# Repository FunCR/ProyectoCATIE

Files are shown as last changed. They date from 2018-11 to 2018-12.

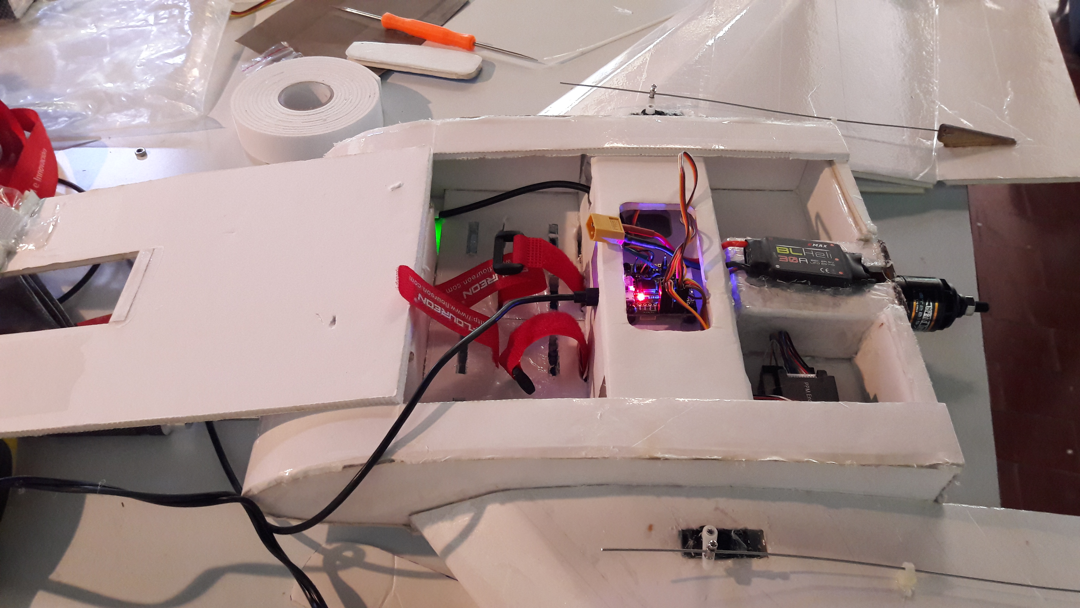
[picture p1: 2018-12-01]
FotosCatie/Montajes del controlador y administrador de energia/Montaje sin Administrador de energia.jpg

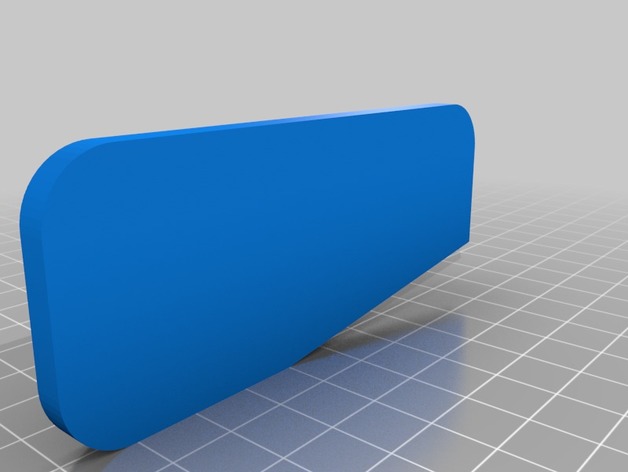
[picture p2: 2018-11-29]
DronAlaFIja/FT_spear_wing_angle_tools/images/22f3830a188973f9ce258d5c663154c2_preview_featured.jpg

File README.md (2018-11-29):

# ProyectoCATIE
Repositorio de documentos, reportes, códigos y archivos digitales de fabricación para el Proyecto FunCR-CATIE

## Directorios

Los directorios en este repositorio contienen todos los archivos del proyecto, desde infromes hasta códigos y diseños para fabricación.

* TreeScan: Archivos del prototipo de escaner de rodales. Incluye diseños fotos y codigos
* QuadLidar: Archivos para el chasis y el dispositivo LIDAR para adaptar al Quad
* DronAlaFija: Archivos de fabricación e instrucciones para la construcción del dron de ala fija
* FotosCATIE: repositorio de fotos del proyecto
* Informes: Informes y documentos generados para el proyecto

Creado por Fundación Costa Rica para la Innovación

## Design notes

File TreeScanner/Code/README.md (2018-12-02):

# Código

* LIDAR_Scanner2: contiene los archivos de programación del microcontrolador en C/C++. Para cargarlo en microcontrolador usar Arduino IDE

* LIDAR_Viewer: Contiene l código en Processing (JAVA), para visualización de datos provenientes del escáner.  El algoritmo comienza a detectar las estructuras grandes, a partir de la cual se pueden determinar árboles.

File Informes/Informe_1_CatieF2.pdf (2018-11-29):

### Informe de acciones basado en la

### Propuesta Conceptual del desarrollo de tecnologías para la

fabricación de instrumentos para la medición de áreas basales, diámetros y altura total, distribución y dispersión de árboles.

Informe elaborado por Tomás de Camino Beck Agosto, 2018

## Índice

Antecedentes | 2
Proceso de Ideación | 3
Validación de Datos con Experto | 3
Revisión de Tecnologías Disponibles | 5
Cuadro Generador de Ideas | 8
Propuesta de Instrumentos | 10
Cronograma | 15
Recomendaciones | 16
Referencias | 16

## Antecedentes

Uno de los retos principales en mensura forestal con el advenimiento de nuevas tecnologías de menor costo y mucho más accesibles, es la de hacer mediciones cada vez rápidas y confiables en campo, y establecer relaciones con variables a nivel de paisaje, que asistan en la toma de decisiones y proyecciones de manejo de bosques.

La tecnología de microcontroladores ha mostrado que se pueden construir instrumentos confiables a gran escala , la discusión ya no está en el “si se pueden

1234
construir”, sino más bien “qué debemos construir”. Inicialmente es más sencillo pensar en tecnologías que reemplazan prácticas de mensura forestal, sin embargo el uso de estas tecnologías probablemente sugerirá nuevas formas de medir variables en bosques, y establecer relación entre variables a escala de rodal y variables a escala de paisaje.

La tecnología LIDAR permite medir distancias mediante un láser que genera pulsos de luz. Esta tecnología que hace algunos años era inaccesible, hoy en día se puede adquiere a costos menores a los $150 y puede ser utilizado para diferentes tipos de medición como altura de árboles . En esta fase nos concentramos principalmente en la

56
exploración de LIDAR y su uso en diferentes contextos

1
""Evaluating the Effects of Projected Climate Change on Forest Fuel ...." http://repository.uwyo.edu/uwnpsrc_reports/vol37/iss1/10/. Se consultó el 31 jul.. 2018.
2
"Digital stereovision system for dendrometry, georeferencing and data ...." https://www.sciencedirect.com/science/article/pii/S1537511018303180. Se consultó el 31 jul.. 2018.

3
"Edge-to-Stem Variability in Wet-Canopy Evaporation From an Urban ...." https://link.springer.com/article/10.1007/s10546-017-0277-7. Se consultó el 31 jul.. 2018.

4
"Observed compression of in situ tree stems during freezing ...." 15 sept.. 2017, https://www.sciencedirect.com/science/article/pii/S0168192317301570. Se consultó el 31 jul.. 2018.

5
"Dense Canopy Height Model from a low-cost photogrammetric ...." 15 feb.. 2016, https://link.springer.com/article/10.1007/s00468-016-1366-9. Se consultó el 31 jul.. 2018.

6
"Comparing Terrestrial Laser Scanning (TLS) and Wearable ... - MDPI." 1 abr.. 2018, http://www.mdpi.com/2072-4292/10/4/540. Se consultó el 31 jul.. 2018.

Este informe no es un tratado científico, sino más bien un reporte de la exploración de posibilidades de uso de tecnologías para generar instrumentos de medición, en particular la medición de diámetros, áreas basales y altura de árboles en un rodal. El objetivo de este proyecto fue Ideación de instrumentos de mensura forestal, específicamente para la medición de diámetros, áreas basales y alturas, a nivel de rodal.

## Proceso de ideación

La ideación consiste en la generación de posibilidades. En este proceso importa la cantidad más que la calidad. Se trabajó revisando la colección de sensores disponibles para poder determinar su posible uso. La exploración de ideas no implica el detalle técnico pues estos se resuelven en el momento de construcción y prototipado de los instrumentos.
Del mismo modo no se detallan aspectos metodológicos para el uso de los instrumento s propuestos, pues las metodologías se establecerán en el momento de prueba de cada uno de los instrumentos.
Las propuestas de instrumentos pueden variar en el proceso de construcción y validación del mismo como parte del proyecto.

Dada la utilizad de tecnologías LIDAR, se exploraron los posibles usos de esta tecnología y la posibilidad de estimar diámetros a través del movimiento del sensor para detectar los bordes de un árbol, incluyéndose alguna forma de posicionamiento relativo con un dispositivo IMU. Por esto en esta fase se explora el potencial de este dispositivo, lo que no descarta usar otras alternativas.

## Validación de Datos con experto

Se realizó una reunión con el Máster Lenin Corrales, investigador del programa de bosques de CATIE Se describieron algunas de las líneas de investigación que el programa quiere desarrollar, para explorar posibilidades de que los resultados puedan ser utilizados para el programa.

La líneas de investigación sugeridas y las posibilidades de usar tecnologías, se resúmen en el siguiente cuadro,

Línea | Tecnología Compatible
Heterogeneidad | Medición de heterogeneidad espacial con Drones
Demografía | Estructura de edades mediante lecturas de clases diamétricas con LIDAR. Crecimiento contínuo con sensores de piezoeléctricos
Fenología (Efecto de cambio climático) | Aunque está fuera de los alcances del proyecto, se podrían construir sistemas de clasificación de especies con inteligencia artificial
Fragmentación y Diversidad | Uso de LIDAR para medir la estructura y distribución espacial de los rodales
Calidad de Cobertura (Sanidad) | Posible aplicación de la fotografía en tiempo real para determinar cambios visibles en superficie de hoja. Explorar la construcción de algunos otros sensores que midan en tiempo real y alta resolución en determinados individuos dentro de un rodal.
NDVI, biodiversidad y conteo de árboles | Tecnología de LIDAR combinada con Drones para medir espectralmente y estructuralmente la composición de especies

## Revisión de Tecnologías disponibles

Tomando en cuenta las tecnologías disponibles para inicio del proyecto, se discutió con el Dr. Ronnie de Camino, especialista en manejo de bosques, los posibles usos en mensura forestal. Estos usos se detallan en el siguiente cuadro.

Equipo | Descripción | Posible uso
Raspberry Pi High-Precision 24bit AD/DA Expansion Board | Extensión para RPi, para poder hacer lecturas de hasta 24bit de resolución | Lector de sensores analógicos y conversión AD de alta precisión
Raspberry Pi | Computadora con sistema operativo Linux | ● Data Logger ● Trap Camera ● Lectura de sensores de alta precisión
Feather M0 Datalogger | Micro-controlador con procesador M0 | ● Data logger ● Lectura de multiples sensores
FeatherWing OLED | Pantalla para microcontrolador | ● Lectura en tiempo real ● Interfaz para usuario de campo
Lithium Ion Polymer Battery -3.7v 1200mAh | Baterías para microcontroladores | ● Sistemas de almacenamiento de datos en campo
SONOFF TH Sensor -DS18B20 | Swith de control remoto | ● Sistemas remotos de encendido y apagado
Adafruit TSL2591 High Dynamic Range Digital Light Sensor | Sensor de Luz | ● Sistemas de medición de luz dentro y fuera del bosque

| | ● Medición de luz visible, ultravioleta e infrarrojo desde el suelo
Adafruit Ultimate GPS Breakout - 66 channel w/10 Hz updates | Sistema de GPS de 10 lecturas por segundo | ● Construcción de GPS portátiles para colocar en dispositivos de campo
ADS1115 16-Bit ADC | Convertidor análogo digital de alta resolución | ● Lectura de instrumentos de medición analógicos de alta presición
Atmospheric Sensor Breakout - BME280 | Sensor de presión, temperatura y altitud | ● Medición de altura sobre el nive del mar, altura de árboles ● Para complementar uso de Drones
Conductive Rubber Cord Stretch Sensor + extras! | Goma que cambia resistencia con estiramiento | ● Medición en timepo real de diámetro
Flame Sensor Module | Sensor de flamas | ● Este sensor mide la radiación infraroja de llamas ● Puede ser utilizadoo para detección temprana de incendios ● detección de zonas calientes
Human Body Touch Sensor | Sensor capacitivo | ● Para construcción de instrumentos de medición
Infrared Thermometer -MLX90614 | Sensor que mide temperatura superficial mediante sensor de luz infrarroja. | ● Temperatura de superficie de suelo bajo diferentes condiciones dentro y fuera del bosque. ● Uso para clasificación de

| | uso de suelo y cobertura con Drone
Liquid Flow Meter 3/4 inch -BRASS | Medido de flujo de líquidos | ● Medición de escorrentía superficial ● Escorrentía en árboles ● Medición de flujo de corrientes de agua
Load Cell - 10kg, Straight Bar (TAL220) | Sensor de peso | ● Medición de Peso de ramás y troncos en sitio
Optical Dust Sensor -GP2Y1010AU0F | Medición de polvo y partículas suspendidas | ● Detector de humo de incendios ● Detector de polvo en campo ● Calidad de aire
Pressure-Sensitive Conductive Sheet (Velostat/Linqstat) | Material conductivo que cambia resistencia con presión | ● Medición de crecimiento en diámetro en tiempo real ● Medición de perturbaciones
Soil Humidity Sensor (Hygrometer) | Sensor de humedad de suelo | ● Medición de humedad de suelo en sitio ● Medición de micro variaciones de suelo ● Medición de evaporación de suelo
Temperature Sensor with Steel Head | Sensor de temperatura | ● Medir temperatura de suelo en tiempo real
Raindrop and Dew Sensor | Sensor de gotas y rocio | ● Medición de evapotranspiración ● Medición de humedad de superficie ● Medición de

| | condensación
Weather Meters | Estación meteorológica de bajo costo. | ● Velocidad de viento ● precipitación, ● temperatura ● presión ● Establecer red de estaciones meteorológicas de bajo costo ● Medición de micro-climas
Adafruit 9-DOF IMU Breakout - L3GD20H + LSM303 | Sistema de navegación | ● Medición de movimiento para Drones ● Determinar posición relativa para medición con LIDAR
Original PRUSA i3 MK2S 3D Printer (Assembled) | Impresora 3D | ● Construcción de estructuras para adaptar sensores ● Construcción de cajas ● Piezas para adaptar sensores a drones

En el proceso de desarrollo como parte de los informes de rendición de cuentas, se analizará algunos ejemplos del mercado para llevar a cabo comparaciones de interés.

## Cuadro Generador de Ideas

Con esta metodología se intenta pensar “fuera de la caja” y forzar el pensamiento lateral para la construcción de ideas. Las ideas generadas acá se dejan planteadas y se pueden desarrollar durante el transcurso del proyecto.

Técnica Ideación | Forma Normal | IDEA

Inversión | Técnico toma datos en campo con cinta diamétrica, clinómetro, etc | Que las mediciones ocurran en tiempo real en el árbol, es decir instrumentos insertado en árboles.
Integración | ärboles tiene placas y son medidos repetidamente, | Árboles base conectados en tiempor real y mandando datos a servidor (SigFox, LoRa) INtegrar en tiempo real con medidas de drones de altura
Extensión | Medir diámetros, áreas basales y alturas | Recoger datos microclimáticos, de terreno. Relacionar directo con dron en aire en tiempo real
Diferenciación | Se usa solamente una metodología de campo | Se miden más variables y por tanto se pueden adaptar medidiones a condiciones especiales
Agregar | MIde AB, diámetro y altura | Medición de diámetro a varias alturas para factor forma. Areas basales a varias alturas.
Restar | MIde AB, diámetro y altura | Con una medida lidar (scan) se derivan las medidas a partir de la imágen generada. Esto hace que el proceso sea de una medición

## Propuestas de Instrumentos

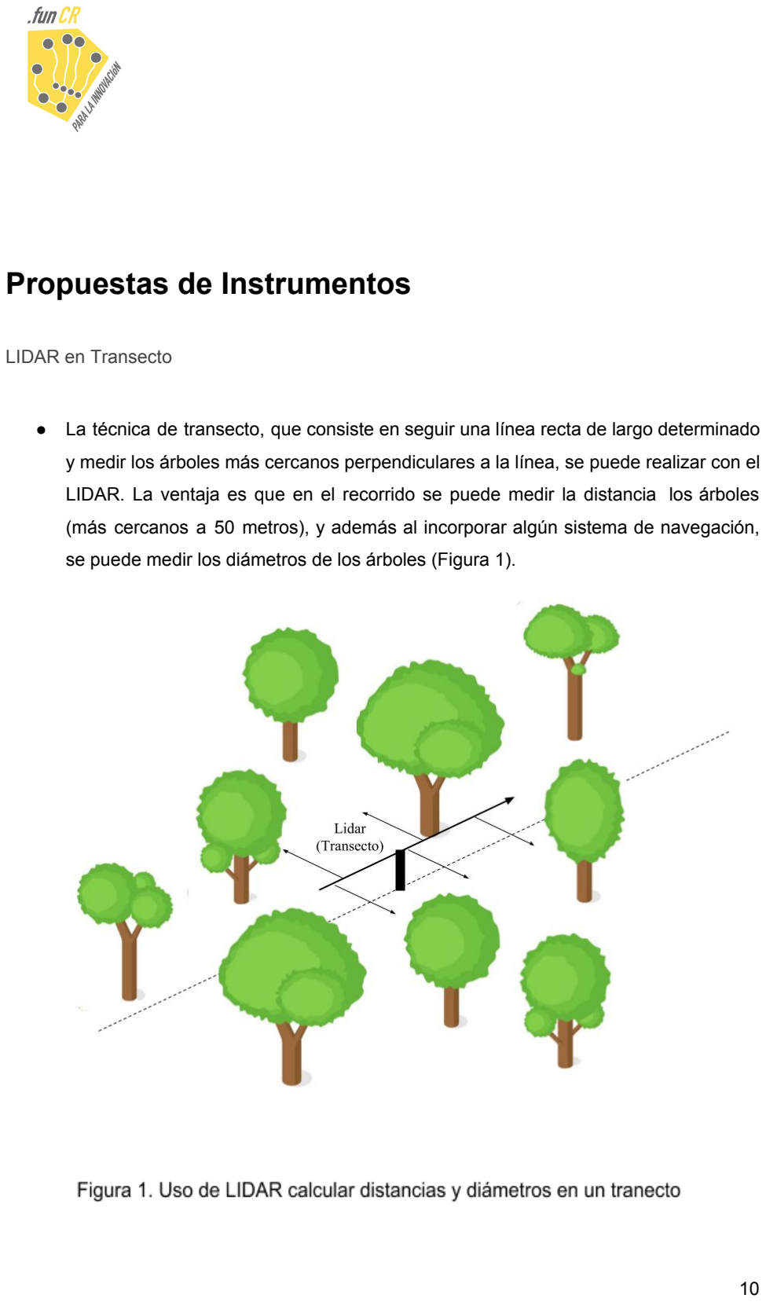
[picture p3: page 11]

LIDAR en Transecto

- La técnica de transecto, que consiste en seguir una línea recta de largo determinado y medir los árboles más cercanos perpendiculares a la línea, se puede realizar con el LIDAR. La ventaja es que en el recorrido se puede medir la distancia los árboles (más cercanos a 50 metros), y además al incorporar algún sistema de navegación, se puede medir los diámetros de los árboles (Figura 1).

- Para construir el dispositivo se debe considerar el uso de 2 LIDAR, y un acelerómetro, giroscopio y compás, para medir el movimiento, la resolución se fija en la frecuencia de lecturas del LIDAR.
- El método de muestreo consistiría en una persona caminando por el transecto demarcado, por la distancia determinada (basada en experiencia de muestreo anteriores (Figura 2).
- El método permitirá medir diámetros rápidamente, y areas basales además de la distribución espacial de los árboles.

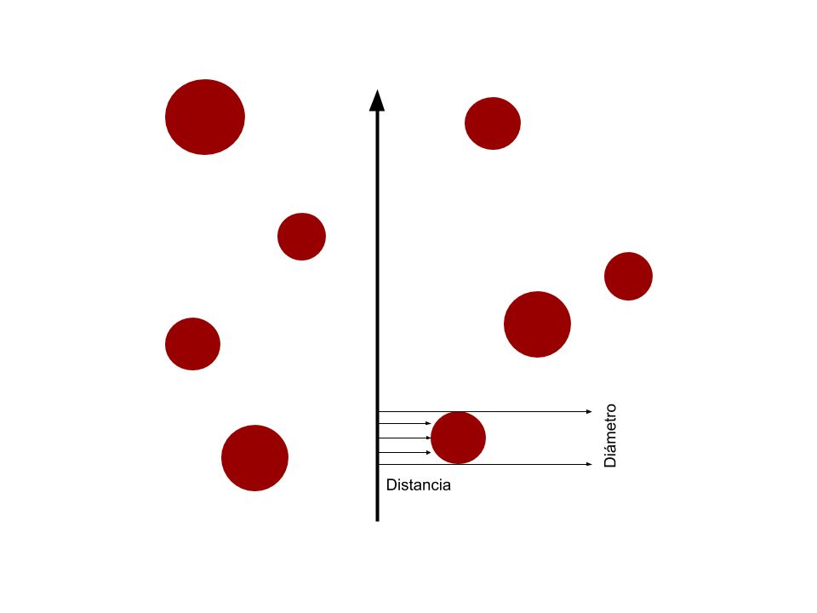
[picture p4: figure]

LIDAR Scan 360

- El lidar montado sobre un motor de paso, que permite rotación de 360 grados, permitiría escanear una nube de puntos en un plano, con la intención de obtener

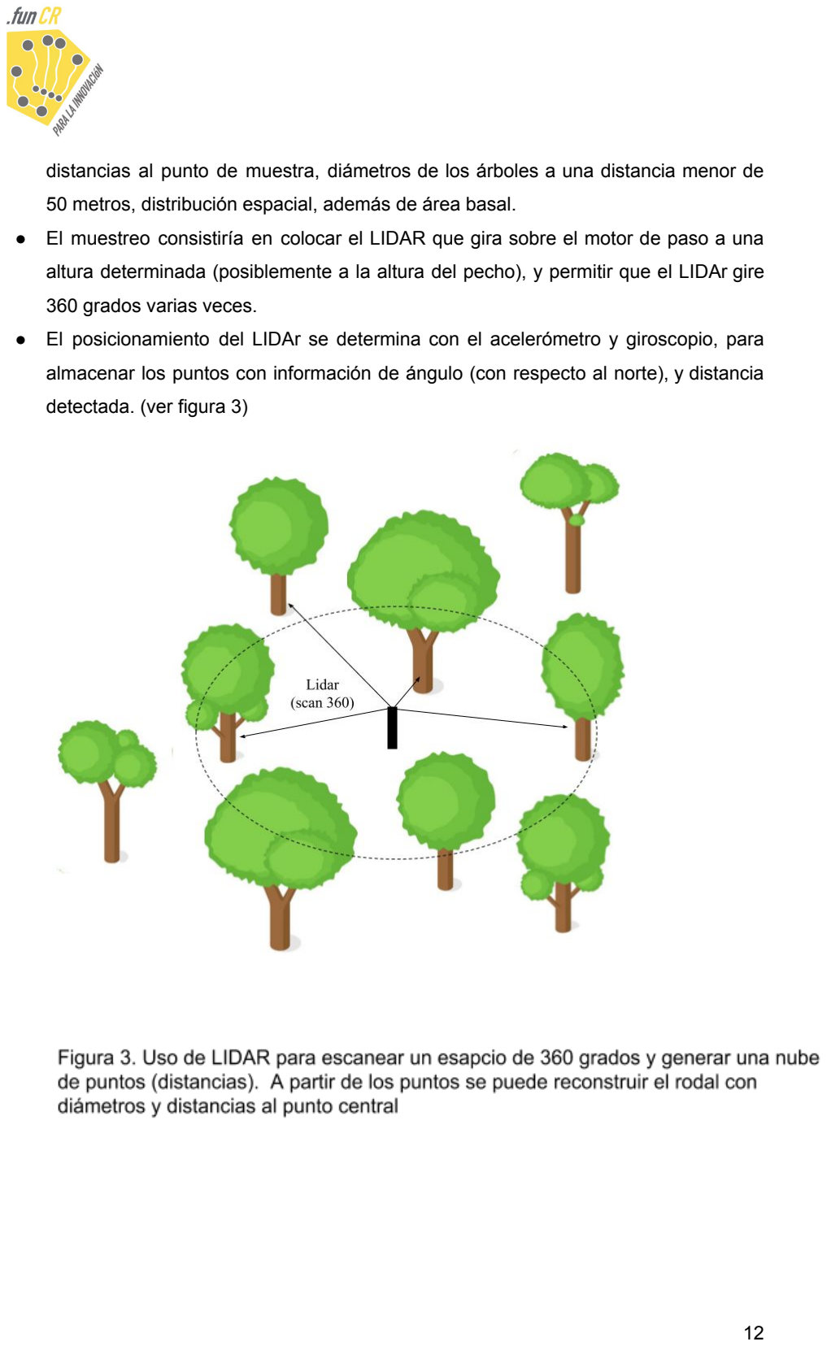
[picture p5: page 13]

distancias al punto de muestra, diámetros de los árboles a una distancia menor de 50 metros, distribución espacial, además de área basal.
- El muestreo consistiría en colocar el LIDAR que gira sobre el motor de paso a una altura determinada (posiblemente a la altura del pecho), y permitir que el LIDAr gire 360 grados varias veces.
- El posicionamiento del LIDAr se determina con el acelerómetro y giroscopio, para almacenar los puntos con información de ángulo (con respecto al norte), y distancia detectada. (ver figura 3)

- Se puede construir un sensor similar al GeoSLAM ZEB-REVO o más sofisticado

7
como el SICK LMS511 que permite escanear una nube de puntos para luego

8
reconstruir una estructura, y algunos ya se han usado para estructura vertical de bosques . La propuesta es construir un sistema, primero en 2 dimensiones, y luego

9
explorar 3D.
- Se prototipará software en porcessing.org para poder reconstruir el rodal en 2D a través de la nube de puntos

LIDAR + Drones para Altura de árboles

Como se muestra en la figura 5, ya se había explorado el uso de un LIDAR adaptado en un drone, con resultados muy preliminares indicando que si era posible medir la diferencia entre copa de árboles y el suelo.

Con el LIDAR y Drone se intentara lo siguiente:
- En vuelo controlado en un recorrido predefinido, se hará un muestreo de la información de lidar para determinar altura de árboles.
- Las alturas se calcularán por línea de vuelo
- Intento de medir un árbol con LIDAR+ drone con verificación desde el suelo
- Medición de alturas conocidas de postes para deterinar presición de medición
- Comparación con medidas de altura de Drone, GPS, y sensores de medición de altura

7
"GeoSLAM Technology - ZEB-REVO - GeoSLAM Desktop V3." https://geoslam.com/technology/. Se consultó el 31 jul.. 2018.

8
"LMS511-10100 PRO | Detection and ranging solutions SICK."
https://www.sick.com/ag/en/detection-and-ranging-solutions/2d-lidar-sensors/lms5xx/lms511-10100-pro/p/p215941. (https://www.sick.com/ag/en/detection-and-ranging-solutions/2d-lidar-sensors/lms5xx/lms511-10100-pro/p/p215941) Se consultó el 31 jul.. 2018.

9
"Efficient field data collection of tropical forest using terrestrial laser ...." https://ieeexplore.ieee.org/document/6946549/. Se consultó el 31 jul.. 2018.

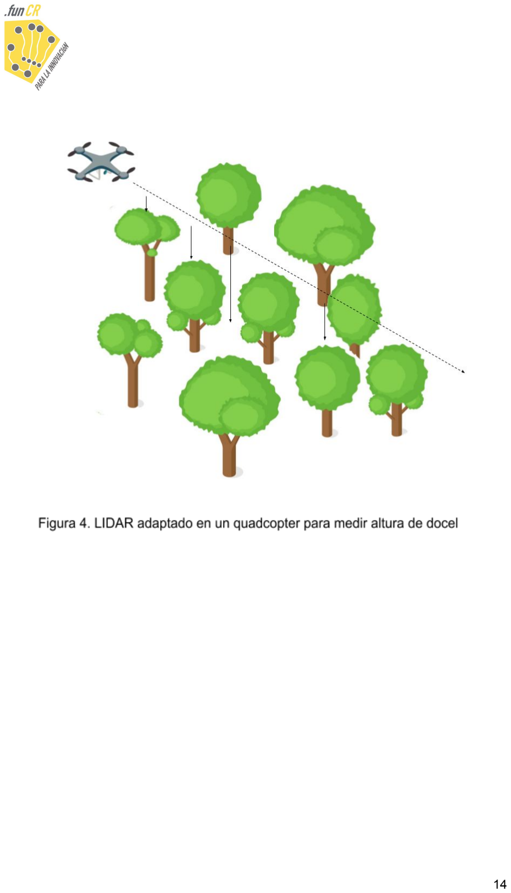
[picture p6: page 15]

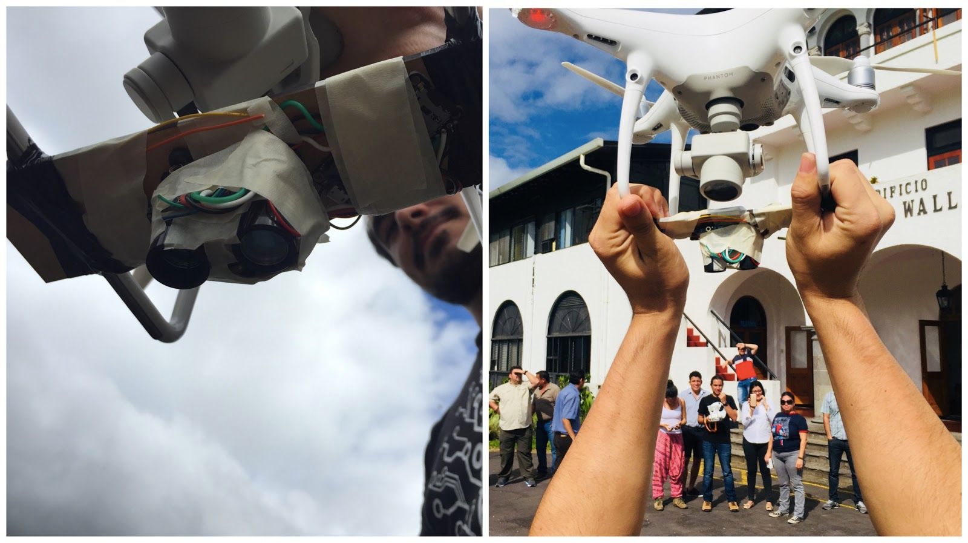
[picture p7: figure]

## Cronograma

Acción | FECHA | LOCACIÓN | ASISTENTES
Prueba de pretotipo en campo, recorrido en el bosque para evaluar características y validar funciones de la tecnología | 3 de setiembre | Turrialba, CATIE | Tomás de Camino Abraham Pineda
Prueba de prototipo de las tecnologías en campo, en dos contextos de bosque definidos por el CATIE. | 20 y 21 de setiembre | Turrialba , CATIE | Tomás de Camino Abraham Pineda
Entrega de prototipo con prueba de campo al equipo de | 8 octubre | Turrialba, CATIE | Tomas de Camino Abraham Pineda

técnico del CATIE

## Recomendaciones

- La construcción de instrumentos de medición se hará con prototipado rápido, es decir se construirá de forma progresiva.
- Se recomienda medir parcelas permanentes de medición, donde los datos sean conocidos y que se hayan hecho mediciones recientemente.
- Utilizar PPM tanto de bosques secundarios como primarios y con algún tipo de aprovechamiento forestal.
- Se debe tener claro que el uso de Drone en bosques puede presentar riesgos de accidente.
- Aunque se proponen estas técnicas, en el proceso puede surgir nuevas ideas que serán exploradas, es decir el resultado de los instrumentos para la siguiente fase puede diferir de lo planteado en este informe.
- Se debe tener claro que este es un proceso de exploración de tecnologías, como tal, las mediciones que se realicen pretenden demostrar las posibilidades tecnológicas, no la construcción de un tratado científico.
- Se debe crear un repositorio de códigos diseños e instrucciones de construcción para poder promover el uso de tecnologías abiertas en la construcción de instrumentos de mensura forestal.

## Referencias

""Evaluating the Effects of Projected Climate Change on Forest Fuel ...." http://repository.uwyo.edu/uwnpsrc_reports/vol37/iss1/10/. Se consultó el 31 jul.. 2018.
"Digital stereovision system for dendrometry, georeferencing and data ...." https://www.sciencedirect.com/science/article/pii/S1537511018303180. Se consultó el 31 jul.. 2018 "Edge-to-Stem Variability in Wet-Canopy Evaporation From an Urban ...." https://link.springer.com/article/10.1007/s10546-017-0277-7. Se consultó el 31 jul.. 2018.
"Dense Canopy Height Model from a low-cost photogrammetric ...." 15 feb.. 2016, https://link.springer.com/article/10.1007/s00468-016-1366-9. Se consultó el 31 jul.. 2018. "Observed compression of in situ tree stems during freezing ...." 15 sept.. 2017, https://www.sciencedirect.com/science/article/pii/S0168192317301570. Se consultó el 31 jul.. 2018. "Comparing Terrestrial Laser Scanning (TLS) and Wearable ... - MDPI." 1 abr.. 2018, http://www.mdpi.com/2072-4292/10/4/540. Se consultó el 31 jul.. 2018.
"GeoSLAM Technology - ZEB-REVO - GeoSLAM Desktop V3." https://geoslam.com/technology/. Se consultó el 31 jul.. 2018.

"LMS511-10100 PRO | Detection and ranging solutions SICK."
https://www.sick.com/ag/en/detection-and-ranging-solutions/2d-lidar-sensors/lms5xx/lms511-10100-pro/p/p215941. (https://www.sick.com/ag/en/detection-and-ranging-solutions/2d-lidar-sensors/lms5xx/lms511-10100-pro/p/p215941) Se consultó el 31 jul.. 2018.
"Efficient field data collection of tropical forest using terrestrial laser ...." https://ieeexplore.ieee.org/document/6946549/. Se consultó el 31 jul.. 2018.

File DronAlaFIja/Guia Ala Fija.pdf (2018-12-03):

### Guia Drones Ala Fija

# Materiales:

- 1 Kit completo cortado en carto-foam, 22 piezas en total.
- 1 Controlador de vuelo, F3 o superior.
- 1 GPS para el controlador de vuelo F3
- 1 Receptor de control remoto de 2.4 Ghz o similar.
- 1 Control remoto de 2.4Ghz o similar
- 1 Administrador de voltaje
- 1 Motor Brushless 2215 de 1050KV o superior
- 1 Controlador de velocidad de 30 amperios o superior para materias de hasta 6 celdas
- 2 Micro servos de 9.5g preferiblemente de engranaje metálico
- 4 Extensiones para servos
- Camara FPV de 600TVL o superior
- Transmisor de video de 5.8ghz de 200 miliwatts a 600 miliwatts
- Module de reception de video en 5.8 Ghz
- Monitor de video para modulo: Pueden ser los lentes Fatshark o los monitores integrados grandes
- Batería de 4 celdas de amenos 2000mah
- Placa para baterias
- Velcro
- Cinta de empaque
- Silicon
- Pistola de silicon caliente
- Cutter
- 2 Alambres de acero inoxidable calibre 20 de 30 cm de largo

# Proceso de ensamble

## Fuselaje

Una vez se cuente con el kit completo del fuselaje en cartón foam, ya sea fabricado a mano o en cortadora Láser, debe seguir el siguiente video instructivo para armar el fuselaje:

https://youtu.be/B5dqMtpdbcU

Existen dos modos de ensamble definidos por si tiene o no administración de energía.

Es necesario poner atención a los diferentes tipos de dobleces en las partes del fuselaje, en el dobles “A” las paredes caen encima de la placa central, en el dobles “B” las paredes quedan al lado de la placa central y el dobles “C” las paredes se doblan una encima de la otra.

## Controlador de Vuelo y Administrador de Energia

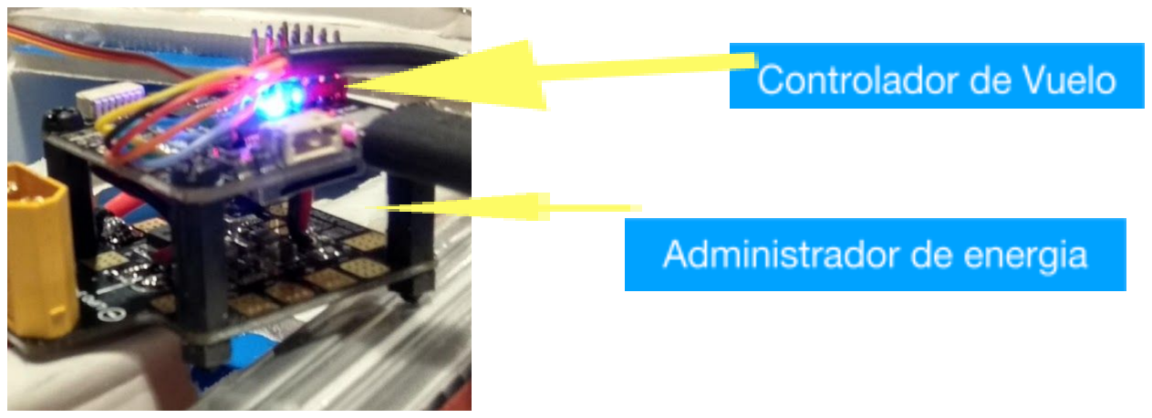
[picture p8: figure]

El video completa la versión del fuselaje preparada para la versión sin el administrador de energía. El administrador de energía y el controlador de vuelo se ensamblan en torre.

## Administrador de energia

El administrador de energía proporciona diferentes voltajes:

- Voltaje directo de la batería para los motores.
- 12 voltios para transmisor de video y tracker GPS.

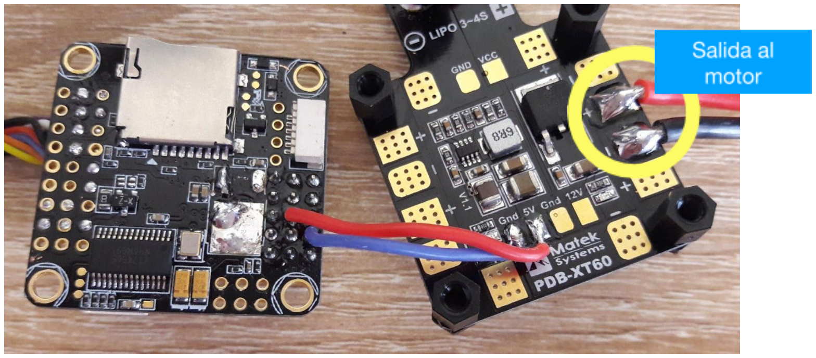
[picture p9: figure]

- 5 voltios para el controlador de vuelo, servos y otros sensores.
*Ensamble del administrador de vuelo con administrador de energía. Conexión de 5v (5 voltios) para controlador de vuelo, sensores y servos y puerto de energía al motor.

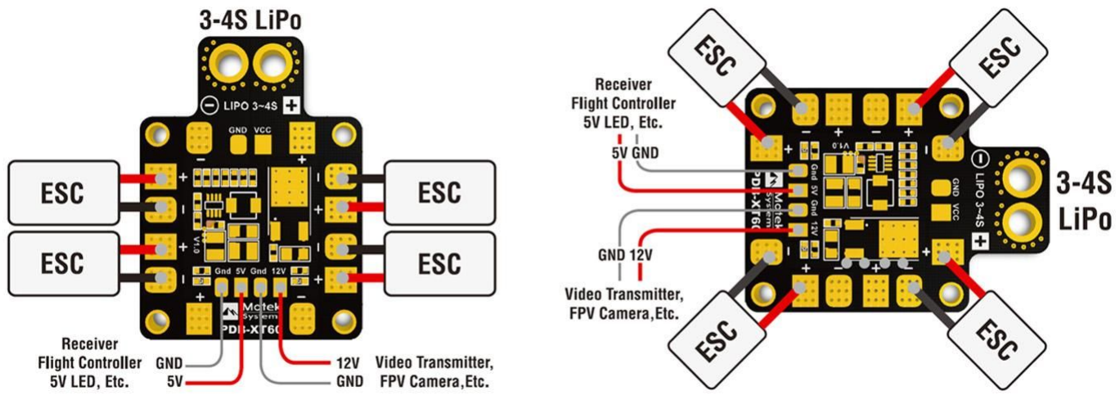
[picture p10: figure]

El administrador cuenta con puertos de energía para los ESC (controladores de velocidad del motor), transmisor de video, controlador de vuelo y otros.
*Ensamble del administrador de vuelo con administrador de energía. Conexión de 5v (5 voltios) para controlador de vuelo, sensores y servos y puerto de energía al motor.
El diagrama muestra todas las posibles conexiiones del administrador, importante tomar en cuenta que todas la conexiones son soldadas. Conectar a todas las cosas según su disposición de vuelo.

El modelo que no contiene administración de energía está dispuesto a ser una fabricación más rápida y un modelo que se puede usar para el entrenamiento de nuevos pilotos o vuelos que no requieren sensores o dispositivos que demanden mucha energía.

El administrador de energía incluye un circuito que filtra la energía para que no existe interferencia entre los diferentes sistemas presentes en el aeronave.

## Controlador de vuelo

El controlador de vuelo que estamos utilizando es de aplicación en carreras de drones, estos drones alcanzan velocidades de hasta 150 Km/h. El diseño de alta precisión y gran velocidad de procesamiento nos permite utilizar este estándar en aplicaciones que explota al máximo las posibilidades de la plataforma mientras entrega un excelente desempeño.

El controlador de vuelo es un Omnibus F3, empaquetado en una versión especial llamada Inav F3. Este controlador está dispuesto para este tipo de aplicaciones autónomas.

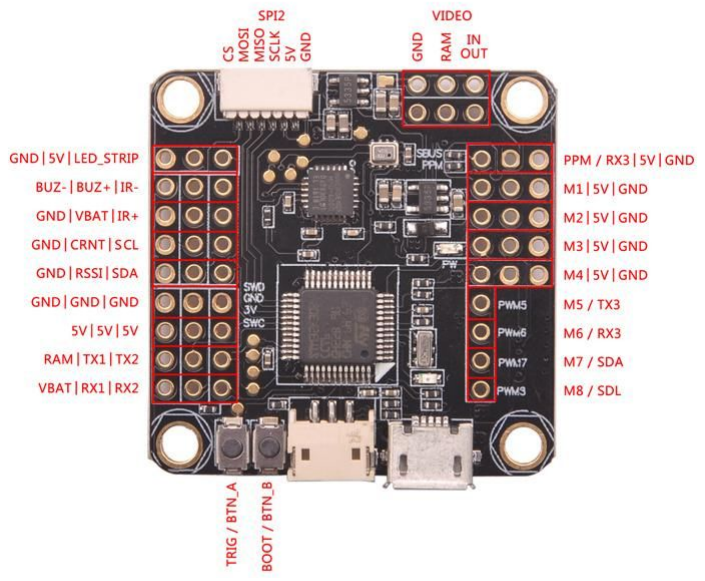
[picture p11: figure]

El diagrama de conexiones es el siguiente:
* Diagrama completo de conexiones.

El controlador de vuelo tiene múltiples tipos de conexión y comunicación:

* Motores: M1, M2, M3, M4 son los que vamos a utilizar en la configuración de ala fija.
* Puerto serial: TX1-RX1 Lo utilizamos para conectar el bluetooth. TX2-RX2 funciona para el GPS
* Puerto I2C( SDA, SCL ): Aca se conecta el magnetómetro externo presente en el GPS.
* Video In -Video Out: Entrada del video de cámara para ser procesado y poner los datos del drone en pantalla y la salida del video procesado.

Actualización de firmware y calibración

Es necesario antes de montar el controlador de vuelo al fuselaje actualizar el firmware del controlador (software de control de vuelo que se corre dentro del controlador) y calibrar los sensores. Todo este proceso se hace con el software Inav. Este se encarga de todo el proceso de calibración, actualización y puesta en marcha del controlador de vuelo.

Descargue he instale software desde este link:

https://github.com/iNavFlight/inav-configurator/releases

En caso de que su computador utilice el sistema operativo Windows por favor Instale los drivers para la tarjeta utilizando la herramienta que encontrará en el siguiente link:

http://zadig.akeo.ie/

Instale la herramienta y siga los siguientes paso:

- Mantenga presionado el botón de boot loader y conecte la tarjeta a su computador usando el cable usb.
- Abra Zadig, escoja Options > List All Devices
- Seleccione STM32 Bootloader, WinUSB
- Haga clic en “replace driver” o “install driver”
Espere a que el proceso termine y continúe.

Para actualizar el software del controlador diríjase a el menú del extremo izquierdo del software y haga clic en “Firmware Flasher”.

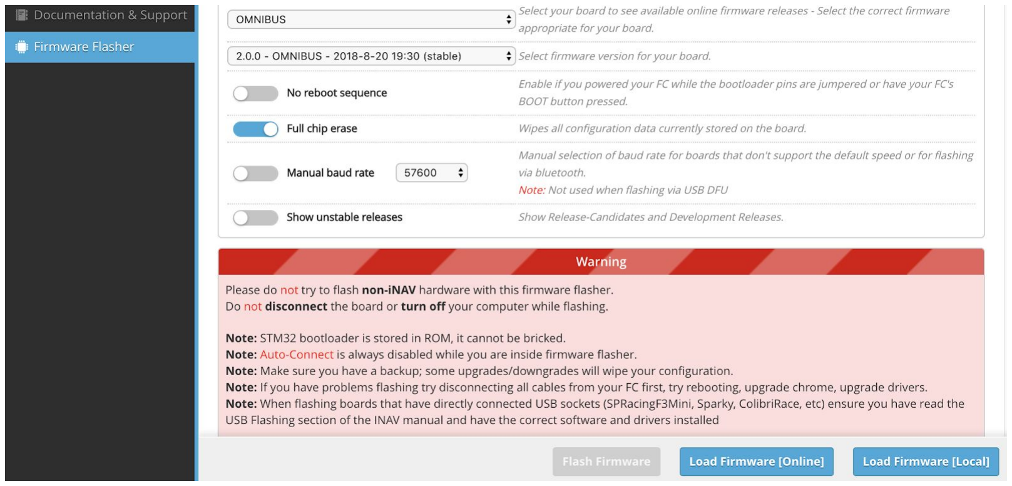
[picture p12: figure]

Seleccione las opciones que muestra la imagen:
Luego click en el botón “Load Firmware [Online]”, una vez termine de cargar el firmware se activará el botón “Flash Firmware”, haga clic en este botón y espere que el sistema le muestre que está listo el proceso.

Ahora con el firmware actualizado haga clic en “Connect”, ahora en el nuevo menú de la izquierda clic en “Calibration” y siga las instrucciones de “Accelerometer Calibration” y “Compass Calibration”.
*Ventana de calibración en “Inav Configurator”.

## Conexión de motor y servos

La configuración de ala fija requiere de un motor para impulsar la aeronave y el uso de servos que a través del alambre de acero mueven los alerones, partes móviles en el final del ala, para darle dirección al ala.

*Diagrama de conexión motores y servos. Los números corresponden a los puertos M1, M2, M3 y M4 del controlador de vuelo.

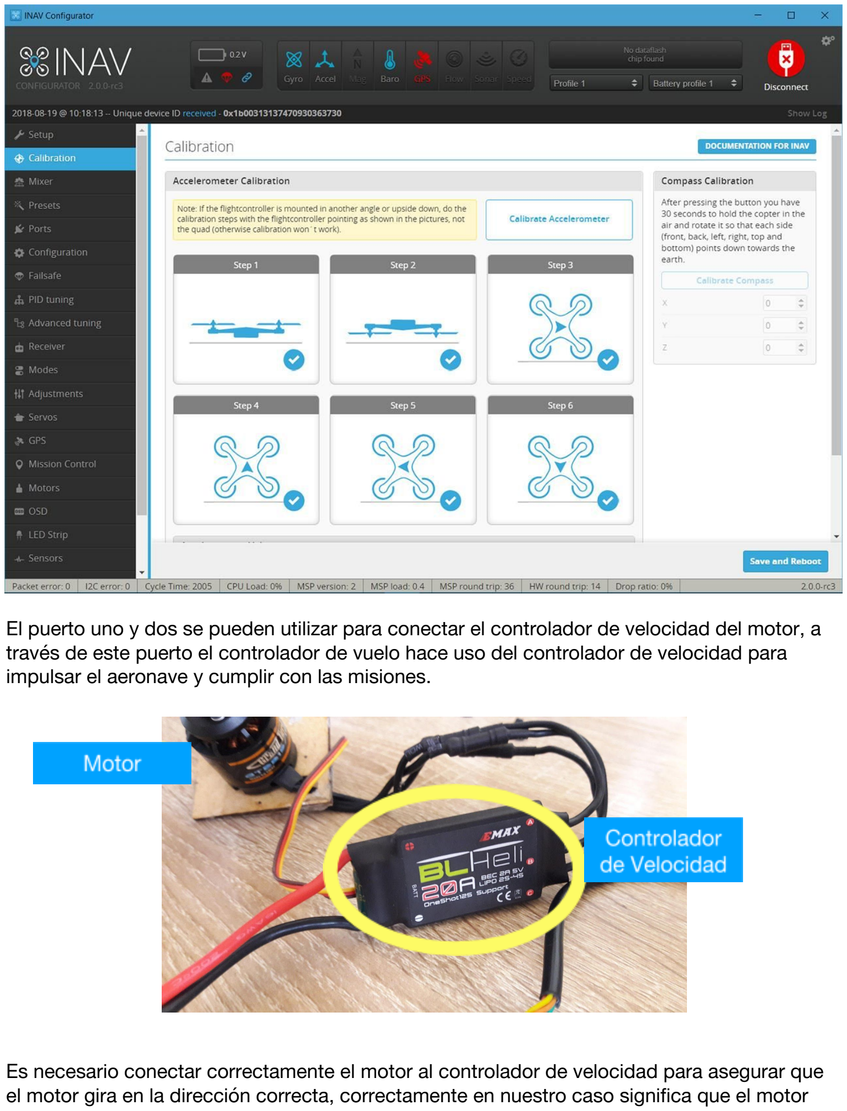
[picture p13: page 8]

El puerto uno y dos se pueden utilizar para conectar el controlador de velocidad del motor, a través de este puerto el controlador de vuelo hace uso del controlador de velocidad para impulsar el aeronave y cumplir con las misiones.

Es necesario conectar correctamente el motor al controlador de velocidad para asegurar que el motor gira en la dirección correcta, correctamente en nuestro caso significa que el motor gira en la dirección que soca la tuerca del eje en el que se monta la propela. En nuestro caso queremos que el motor gire contra las manecillas del reloj.

Este es un proceso de prueba y error. Lamentablemente no
todos los controladores de velocidad están montados igual y
los motores no tienen el mismo embobinado.

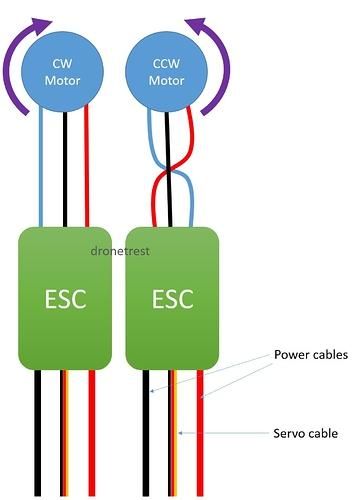
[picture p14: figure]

## Este proceso se debe de hacer sin tener

la propela instalada.

El primer paso es conectar los cables uno a uno de forma paralela, acto seguido se conecta el cable de control del ESC ( electronic speed controller - controlador de velocidad) a un recibidor del control remoto en el canal del Throttle (potencia) y se mueve la palanca de ese canal para mover el motor.

En caso de que el motor gire en sentido erroneo se invierte la conexión de los cables de los extremos, el centro se mantiene.

* Diagrama muestra cómo invertir los cables para cambiar la dirección del motor, dirección puede variar según el ESC y el motor. Imagen tomada de dronetrest.com.

Los servos se conectan a los puertos M3 y M4, el servo de la izquierda en el M3 y el de la derecha en M4.

Tal como lo muestra el diagrama de de conexión de motores.

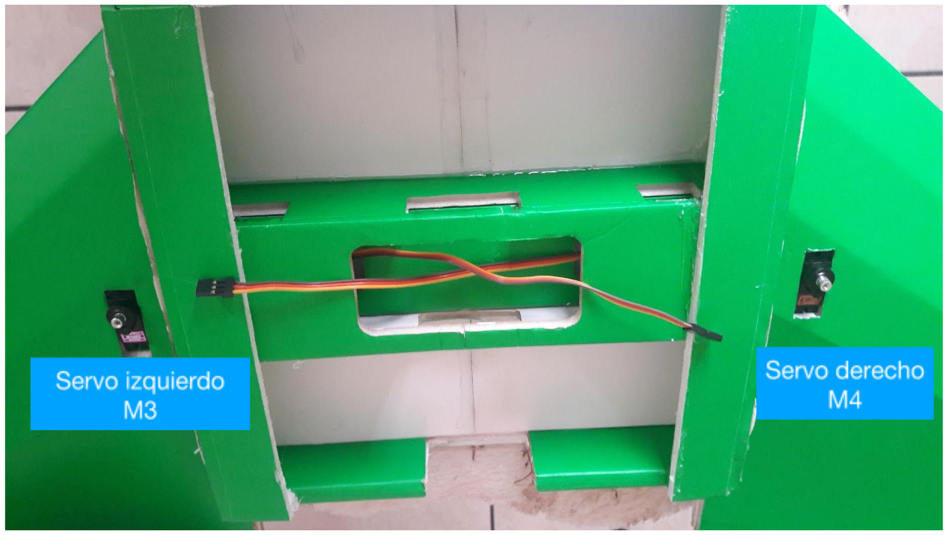
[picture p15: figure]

## Recibidor del control remoto

En nuestro controlador de vuelo el recibidor del control remoto utiliza el protocolo de comunicación PPM, mas información en este link https://en.wikipedia.org/wiki/Pulse-position_modulation. Y se conecta en el puerto PPM del controlador de vuelo.

Una vez esto está hecho debemos dirigirnos al menú de la izquierda en el botón “Receiver”, si el recibidor está correctamente conectado a el puerto PPM usted verá las lecturas del recibidor moverse al mover las palancas y switches del control.

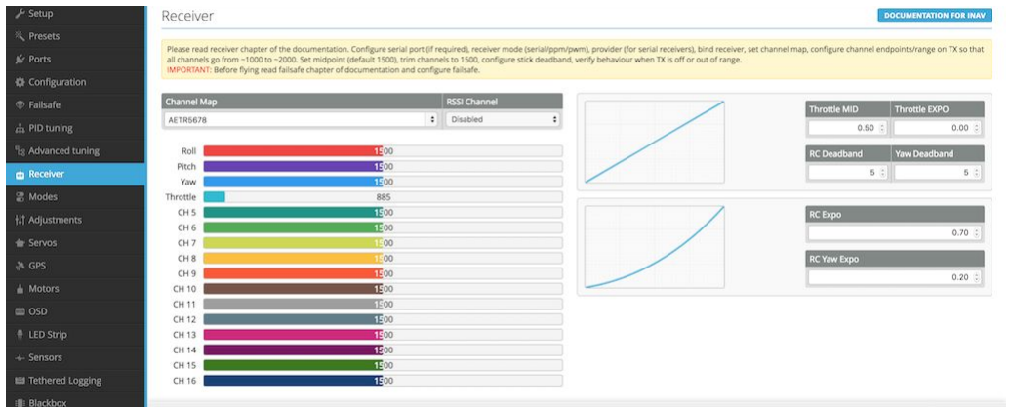
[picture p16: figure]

Si esto funciona correctamente tenemos que configurar los extremos y centros de la señal.

*Lecturas del recibidor del control remoto en “Inav Configurator”.
Cuando las palancas del control se encuentran el los centros la lectura en el software debe ser de 1500. Es normal que la lectura “brinque” un poco entre números cercanos. Si esto no es así debe de corregirlo desde el control remoto. Todo control remoto es diferente refiérase al manual del fabricante para saber como corregir el “Sub-trim” de cada canal. Al hacer cambios en el control estos se reflejaran en la interfaz de Inav.

Cuando las palancas de encuentran en el extremo mínimo la lectura en el software debe ser de 1000 y cuando está en el extremo máximo debe ser de 2000. Si esto no es así debe de corregirlo desde el control remoto. Todo control remoto es diferente refiérase al manual del fabricante para saber como corregir el “Channel Endpoints” de cada canal. Al hacer cambios en el control estos se reflejaran en la interfaz de Inav.

Puede referirse a estos links para ver algunos detalles:

https://github.com/iNavFlight/inav/blob/master/docs/Rx.mdhttps://www.youtube.com/watch?v=nDsNWZgxmw4

# FailSafe - Procedimiento de emergencia

El Failsafe es la herramienta que nos permite decidir cómo se va a comportar el aeronave en caso de que pierda conexión con el control o la estación base.

Es este caso deseamos que el failsafe se active en caso de que se desconecte del control y no este ejecutando una navegación autónoma.

Para configurar esta característica es necesario ver la ventana del recibidor en Inav Configurator y una ver abierta asegurarse de que tenemos conexión con el control, este se sabe al mover las palancas del recibidor y los valores de los canales cambian en el software.

Una vez asegurado esto, el siguiente paso es apagar el control remoto y ver el cambio en las lecturas de la pantalla del recibidor. Todo recibidor de control remoto tiene un failsafe interno, que cambia la lecturas que envía para hacerle saber al controlador de vuelo que perdió conexión con el control, en algunas ocasiones es posible modificar el comportamiento de este failsafe, consulte el manual del fabricante.

Al apagar el control tome nota de cuál es la lectura más baja y más alta de los canales que antes estaban activos.

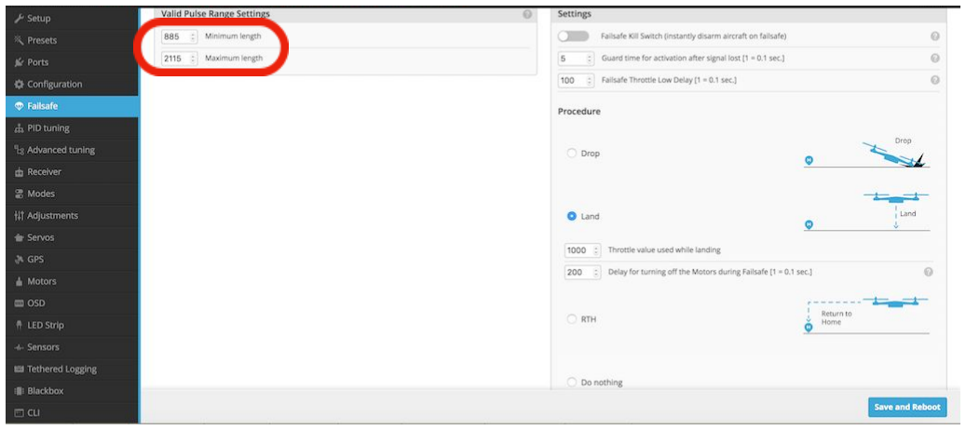
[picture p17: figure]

Ahora diríjase al menú de la izquierda y haga click en “Failsafe”, y en el espacio de “Minimun length” poner la lectura más baja y en el de “Maximum length” la lectura más alta.

En “Procedure” haga clic en RTH, que significa Return to home. Esto significa que el aeronave volverá al punto del que despegó.

## GPS

El Módulo de GPS viene soldado a la place Inav F3, conectado al puerto serial número 2 tal y como lo vimos al inicio de esta guía.

Ahora diríjase a la ventana de “Ports” y en línea de “UART 2” y la columna de “Sensors” escoja la opción “GPS”.

Ahora en la ventana de Configuración active el GPS deslizando el Switch hacia la derecha.

## Instalación de controlador de vuelo en el fuselaje

Una vez el controlador de vuelo se encuentre instalado con administrador de energía (en la configuración que lo incluye), controlador de velocidad, GPS y recibidor de control remoto. El paso siguiente es instalarlo en el centro del fuselaje.

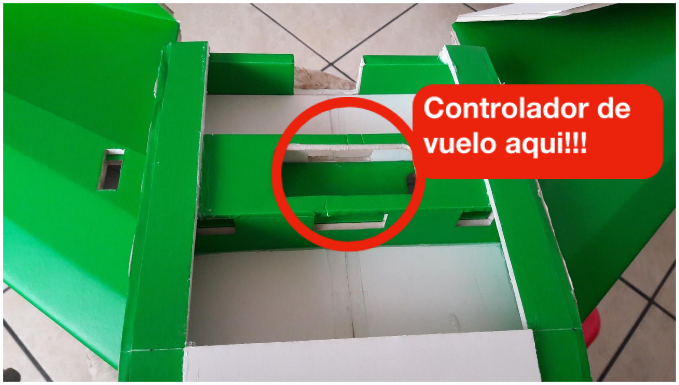
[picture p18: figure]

El compartimiento del centro del fuselaje es el lugar idoneo para ubicar el controlador.

Esta es la zona más cercana al centro de gravedad del fuselaje y por ende el mejor lugar para que los sensores del controlador de vuelo tengan las lecturas más eficientes.

## Ejemplo de instalación

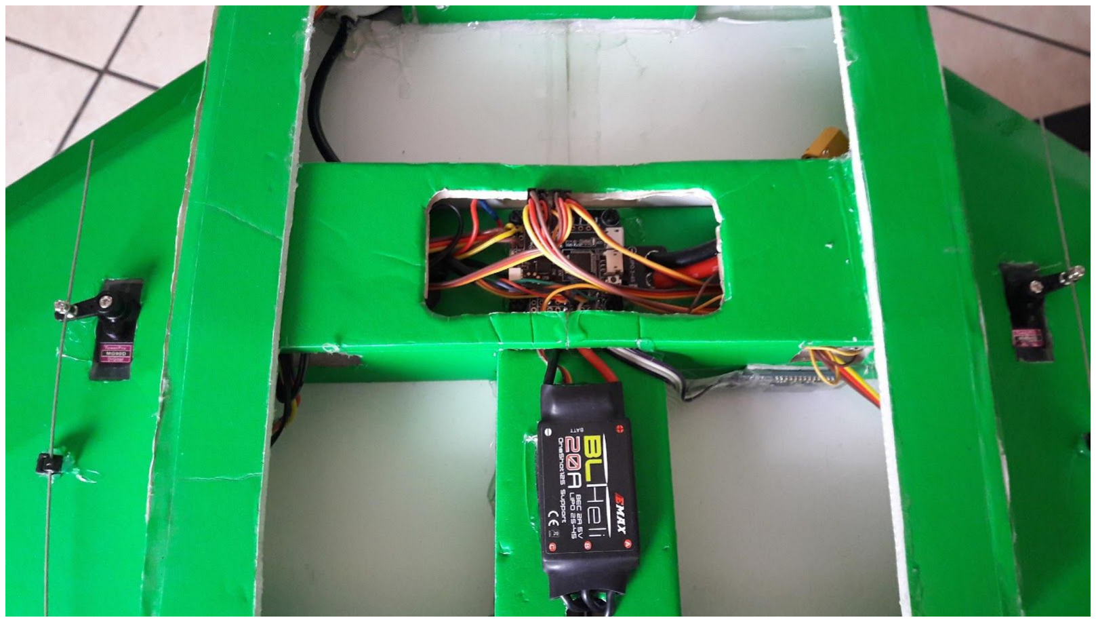
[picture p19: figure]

## Configuración especifica del software

Es necesario correr algunas configuraciones especificas para el ala fija. El el menú de la izquierda en Inav Configurator el último ítem dice “CLI” haga click en el botón. CLI significa “Command Line Interface”

Al ingresar a la ventana en la parte de abajo verá un renglón blanco en el cual puede escribir o pegar comandos, por favor copie los siguientes comandos, peguelos en el renglón blanco y presione enter:

set max_angle_inclination_rll = 600
set max_angle_inclination_pit = 600
small_angle = 180
set nav_rth_altitude = 8000
set nav_rth_alt_mode = CURRENT set nav_rth_allow_landing = NEVER
set align_mag = CW270_DEG_FLIP
set align_board_pitch = 10

Ahora se encuentra listo para su primer vuelo de prueba.

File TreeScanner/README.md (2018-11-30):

# Tree Scanner

 * Todos los archivos prototipos y códigos para el scanner de árboles. Proyecto CATIE
 * El directorio CATIEdata contiene los datos obtenidos en las primeras pruebas de escabeo de un rodal de bosuqe secundario

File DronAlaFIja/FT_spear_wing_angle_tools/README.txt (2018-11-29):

                   .:                     :,                                          
,:::::::: ::`      :::                   :::                                          
,:::::::: ::`      :::                   :::                                          
.,,:::,,, ::`.:,   ... .. .:,     .:. ..`... ..`   ..   .:,    .. ::  .::,     .:,`   
   ,::    :::::::  ::, :::::::  `:::::::.,:: :::  ::: .::::::  ::::: ::::::  .::::::  
   ,::    :::::::: ::, :::::::: ::::::::.,:: :::  ::: :::,:::, ::::: ::::::, :::::::: 
   ,::    :::  ::: ::, :::  :::`::.  :::.,::  ::,`::`:::   ::: :::  `::,`   :::   ::: 
   ,::    ::.  ::: ::, ::`  :::.::    ::.,::  :::::: ::::::::: ::`   :::::: ::::::::: 
   ,::    ::.  ::: ::, ::`  :::.::    ::.,::  .::::: ::::::::: ::`    ::::::::::::::: 
   ,::    ::.  ::: ::, ::`  ::: ::: `:::.,::   ::::  :::`  ,,, ::`  .::  :::.::.  ,,, 
   ,::    ::.  ::: ::, ::`  ::: ::::::::.,::   ::::   :::::::` ::`   ::::::: :::::::. 
   ,::    ::.  ::: ::, ::`  :::  :::::::`,::    ::.    :::::`  ::`   ::::::   :::::.  
                                ::,  ,::                               ``             
                                ::::::::                                              
                                 ::::::                                               
                                  `,,`

https://www.thingiverse.com/thing:2586017
FT spear wing angle tools by Viceroy86 is licensed under the Creative Commons - Attribution license.
http://creativecommons.org/licenses/by/3.0/

# Summary

FT spear angle tools to get wing angle right, one is with 27 and 21 angle and the other part is 8,5 angle, hope this helps someone.

# Print Settings

Printer: Creality CR-10
Rafts: Doesn't Matter
Supports: No

Notes: 
Simple to make just print it your normal settings

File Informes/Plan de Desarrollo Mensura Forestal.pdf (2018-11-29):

## Desarrollo de instrumentos de mensura forestal para el

## monitoreo de bosques secundarios

Tomás de Camino Beck¹

## Introducción

El manejo eficiente y efectivo de bosques naturales, está directamente relacionado a la calidad de datos recolectados para poder construir modelos predictivos de aprovechamiento y recuperación. Los inventarios forestales que se realizan a nivel de muestreos de campo, han sido importantes para poder desarrollar buenos planes de manejo, es claro entonces que hacer tanto más eficientes como más precisos los datos obtenidos de estos muestreos, pueden tener un impacto positivo en el desarrollo de prácticas forestales más efectivas (Goodbody et al. 2017).

La toma de datos lleva implícita la necesidad de utilizar instrumentos de medición de cambios tanto a nivel de árboles individuales como a nivel de cobertura. La evolución de la instrumentación científica para mensura forestal, generalmente ha estado dominada por la disponibilidad y accesibilidad comercial de instrumentos, más que por el desarrollo de instrumentos que se ajusten a la necesidad de muestreo. Sin embargo, para lograr medidas precisas y costo-efectivas, es necesario la creación de instrumentos nuevos, que permitan adaptarse a las prácticas de mensura forestal, para permitir tomar mayor cantidad de muestras en un tiempo menor.

En la última década, gracias a la aparición en el mercado de microcontroladores de bajo costo como Arduino , y versiones genéricas de sensores, se hace posible la construcción de ² instrumentos de medición científicos de alta precisión a bajo costo y adaptado a las

1 Fundación Costa Rica para la Innovación. Reporte parte del proyecto para el desarrollo de instrumentación forestal entre CATIE y la Fundación Costa Rica para la Innovación
2 Arduino es una marca de microcontroladores de bajo costo. Un microcontrolador es una pequeña computadora que permite tomar información de sensores y poner a funcionar diferentes tipos de actuadores en respuesta, o tomar datos y almacenarlos.
BORRADOR necesidades de los investigadores (ver por ejemplo D’Ausilio, 2012, Silja, 2016). Más aún, las investigaciones científicas, pueden plantear las necesidades de medición de variables y luego construir instrumentos para medirlas, y no lo inverso, donde la mayoría de investigaciones a nivel de bosques dependen del desarrollo de instrumentos comerciales de medición.

Adicionalmente, la construcción de instrumentos propios es de menor costo, Así por ejemplo una estación meteorológica comercial portátil puede rondar los $1500 (de la marca HOBO), una basada en tecnología Arduino tiene un costo menor a $200 (Sparkfun), y puede ser utilizado para desarrollar propiedad intelectual en la construcción de instrumentos científicos, que pueden llevar a el desarrollo de modelos nuevos de financiación de investigación (Akram Syed et al. 2016, Pearce 2012, 2013, Perrine 2017).

Por otro lado, la popularización y la reducción de costos de drones también han permitido la ³ incorporación de técnicas de exploración y monitoreo remoto, utilizando los drones como base, en las investigaciones forestales (Lina et al 2015). Las aplicaciones son muchas, desde el monitoreo de bosques (Koh and Wich, 2012), Medición de altura de bosques (Siebert and Teizer 2014, Mid Mohan et al. 2017), fotogrametría (Ota et al. 2017) y en general manejo de bosques (Lina et al 2015). Sin embargo, es indispensable pensar en el dron, como una plataforma de desarrollo para mejorara las prácticas forestales, y no como un producto de consumo que aumente la complejidad en las estrategias de manejo forestal.

Como parte del esfuerzo para explorar el manejo y aprovechamiento de bosques secundarios, se inició un proyecto de desarrollo de instrumentación forestal tanto a nivel de bosque como a nivel de cobertura, utilizando tecnologías de fuente abierta y de bajo costo. El programa comienza con la exploración del uso de sensores, procesamiento y almacenamiento de datos de campo, a través de tecnologías basadas en arduino, así como la construcción de drones de bajo costo para el monitoreo de bosques secundarios. El objetivo del programa parte de la construcción de instrumentos de medición forestal, para mediciones a nivel de campo, hasta la creación de metodologías con drones para mediciones a nivel de cobertura forestal. Como

3 Denominamos “drone” a un vehículo de vuelo autónomo o operado por un piloto que no se encuentra a bordo del vehículo. Esto incluye quadcopters, rovers y planeadores de ala fija resultado se espera no sólo construir herramientas funcionales, sino documentar y transferir estas experiencias para su uso libre, y bajo la filosofía open source, permitir un desarrollo y mejoría de estos a través de una comunidad de usuarios.

En este documento se describen las experiencias del primer taller realizado con participantes de 4 países centroamericanos, a partir del cual se propone un plan de desarrollo para muestreos de campo, como para incorporarlos en Drones para monitoreo remoto y medición de cobertura.

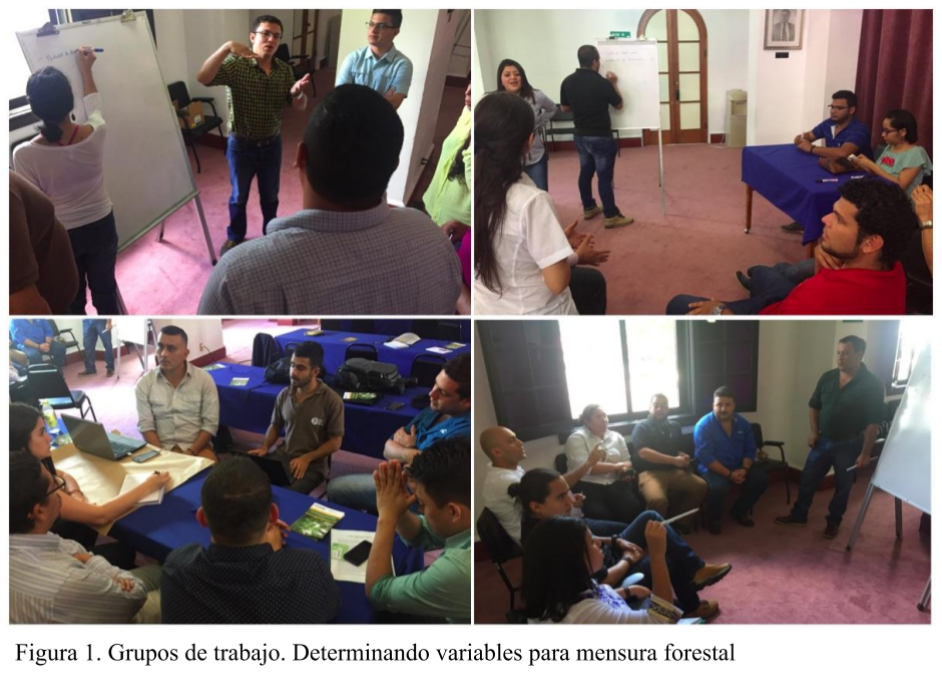
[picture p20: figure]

## Plan de desarrollo

Es importante recordar que este es un proceso de experimentación en el desarrollo de componentes de medición, por esa razón, los costos son aproximados, y la inversión se hace de forma progresiva a medida que se van construyendo drones e instrumentos, y se van encontrando obstáculos y necesidades en el proceso. Así por ejemplo, la investigación en vuelo de drones implica posibles accidentes en vuelo, o corto circuitos en la construcción, lo cual puede implicar tener que reemplazar componentes dañados. Los montos indicados son aproximados pero se definen como límite superior.

También es posible que en el proceso de desarrollo se detecten nuevas direcciones que puedan ser valiosas de explorar, es decir este tipo de investigación implica mucha incertidumbre en los posibles resultados. Es claro que se obtendrán instrumentos de alto nivel de medición, lo que no es claro es la ruta exacta que nos va a llevar a dichos resultados.
Se inicia con el desarrollo de instrumentos, y en el proceso de prototipa y prueba software para la integración de información. En una etapa posterior se desarrollarán versiones finales de software.

### Objetivo General:

Desarrollar instrumentación para asistir y acelerar los procesos de inventarios y monitoreo de bosques secundarios.

### Objetivos Específicos:

1. Desarrollo de instrumentación para medición de áreas basales, diámetros y altura de bosques, distribución y dispersión de árboles.
2. Desarrollo y prueba de drones de ala fija para el monitoreo de bosques, fotogrametría, y recolección de datos
3. Modificación de drones comerciales para la medición de altura de bosques
4. Prototipado de software para integrar información y determinar variables de manejo forestal (crecimiento, volúmenes)

### Ruta Crítica

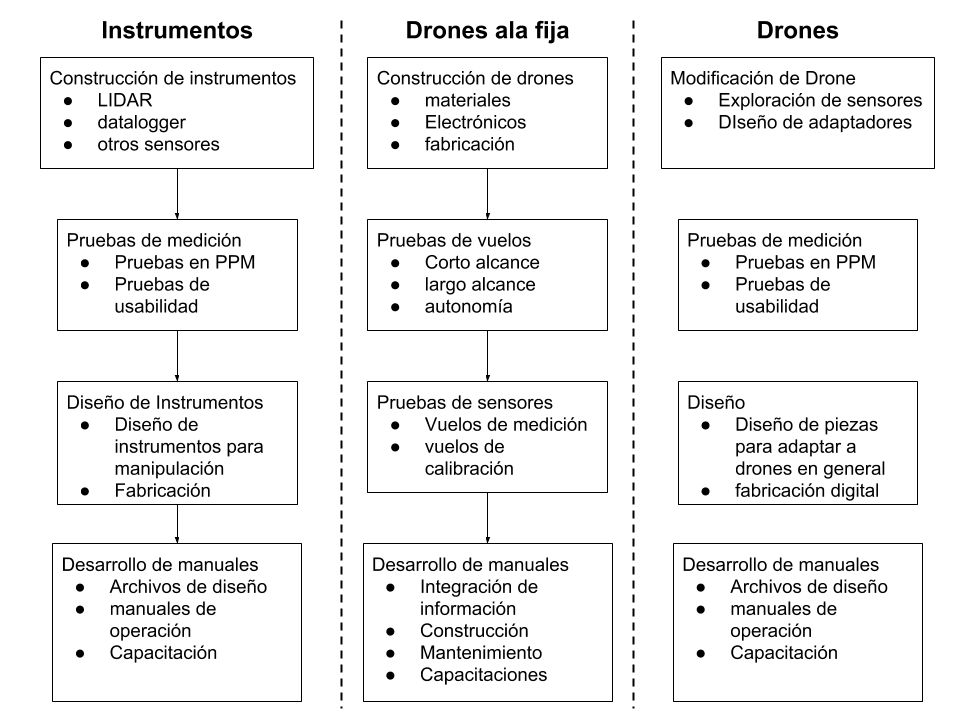
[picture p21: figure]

### Instrumentación

El esquema de la figura, muestra la estrategia de medición utilizando LIDAR y otros sensores biofísicos que se recomienda desarrollar. Son 4 funciones principales del instrumento basado en el LIDAR lite 3 y otros sensores, que permite medir distancias con alta precisión de hasta 50 metros:

1. Medición de diámetros
2. Medición de área basal de un rodal
3. Medición de altura de un árbol
4. Medición de altura de dosel

Para lograr un uso efectivo del LIDAR y otros senosres, se propone la prueba del sensor LIDAR lite, incorporando un navegador inercial de 9 grados de libertad, de esa manera los movimientos de “escaneo” de árboles, se basan en un sistema de referencia de punto muerto y de esa manera se puede escanear una nube de puntos del rodal, para general un modelo tridimensional, para posterior análisis matemático y estadístico. También se explorarán otros sensores de rango, y de medición de distancias

Objetivo: Desarrollo de un instrumento de medición de diámetro, área basal y altura de árboles, basado en tecnología LIDAR, sensores de rango y de movimiento .

Materiales necesarios:
1. Impresora 3D
2. Micro-controladores y sensores varios
3. LIDAR lite (y otros posibles sensores de rango)
4. Dispositivo IMU

Cronograma:

Acción | Mes 1 | Mes 2 | Mes 3 | Mes 4 | Resultado
Exploración de tecnologías LIDAR y | | | | | Pruebas de concepto de diferentes tecnologías, primeros prototipos de

otros sensores y de navegación | instrumentos
Pruebas de instrumentos en campo | Mediciones preliminares comparadas con métodos tradicionales. Determinar la precisión de nuevos instrumentos, y el tiempo de medición
Rediseño de versiones mejoradas, y construcción de primeros instrumentos | Mejoramiento de diseños, y construcción de instrumentos para uso real
Publicación y documentación abierta de instrumentos | Domentación para garantizar replicabilidad de instrumentos y permitir desarrollo open source

Inversión necesaria:

Rubro | Inversión
Componentes (impresión 3D, LIDAR y otros componentes electrónicos, sensores varios y accesorios, suministros de impresión 3D) | $5000
Giras a campo (2 Giras, 3 días cada una) | $6000*

*inversión no incluye viaticos.

### Desarrollo de drones de ala fija

Objetivo: Construcción de drones de ala fija, con sensores de imágenes y lidar, además de transmisores de radio

Materiales necesarios:
1. Impresora 3D
2. Materiales de construcción de drones (cartofoam, tape y otros materiales)
3. LIDAR lite (y otros posibles sensores de rango)
4. Micro-controladores y sensores varios

5. Cámaras con sensores infrarrojos y visibles (Cannon S110)
6. Componentes de drones (motores, controladores, control de navegación, componentes de navegación autónoma)

Cronograma:

Acción | Mes 1 | Mes 2 | Mes 3 | Mes 4 | Resultado
Construcción de Drones | | | | | Fabricación de drones con cortado láser y rpuebas de vuelo
Pruebas de campo de medición | | | | | Pruebas de vuelo y medición de campo de varios bosques (principalmente parcelas permanentes)
Análisis de resultados y publicación | | | | | Construcción de documentos y publicación de resultados

Inversión necesaria:

Rubro | Inversión
Materiales de construcción componentes de drones Sensor remoto Cannon s110 Lidar Controladores de vuelo autónomo Componentes de navegación | $10000
Giras a campo (1 gira 4días) | $4000*

*inversión no incluye viaticos.

### Medición de altura de árboles

Objetivo: Pruebas de medición LIDAR en bosques secundarios, utilizando quadcopter y LIDAR

Materiales necesarios:
1. Impresora 3D
2. Micro-controladores y sensores varios

3. LIDAR lite (y otros posibles sensores de rango)
4. Quadcopter

Cronograma:

Acción | Mes 1 | Mes 2 | Mes 3 | Mes 4 | Resultado
Adaptación de LIDAR a drone (piezas 3D, programación de GPS y datalogger) | | | | | Construcción de una estructura para adaptar el LIDAR al drone
Pruebas de campo | | | | | Pruebas de vuelo y medición de campo de varios bosques (principalmente parcelas permanentes)
Análisis de resultados y publicación | | | | | Construcción de documentos y publicación de resultados

Inversión necesaria:

Rubro | Inversión
Componentes (impresión 3D, LIDAR y otros componentes electrónicos y accesorios, suministros de impresión 3D) | $1000
Giras a campo (1 gira, 3 días) | $3000*

*inversión no incluye viaticos.

## Conclusiones y Recomendaciones

- Más que solamente construir unos pocos instrumentos de medición, es más importante dejar la experiencia y capacidad para adaptar y desarrollar los instrumentos según se necesiten
- La publicación de detalles técnicos puede ser más importante que la publicación de resultados científicos, dado que aunque muchos resultados con el uso de nuevas tecnología son interesantes, el potencial está en el proceso de adquisición de datos con nuevas tecnologías.

- El objetivo más importante del taller no era el de tomar datos, sino el de explorar las posibilidades de uso de nuevas tecnologías y el de estimular a la comunidad de forestales a que intenten desarrollar sus propios instrumentos
- Para garantizar el éxito del proyecto es necesario hacer un estudio comparativo de las mediciones con nuevas tecnologías con respecto a anteriores, y determinar qué tan rápido se pueden realizar para mejorara y agilizar los inventarios forestales.
- La inversión inicial de construcción de drones puede ser alta, debido a la necesidad de comparar varios componentes para poder luego determinar las mejores opciones para el diseño final
- El objetivo de la exploración de drones de ala fija es la de encontrar un modelo de construcción de bajo costo, que permita obtener información de fotografías y cualquier otra variable biofísica a bajo costo y de manera frecuente.
- Una vez desarrollado los drones, es importante realizar una investigación fotogramétrica con los drones de ala fija. Para ello se sugiere una investigación básica de fotointerpretación y de obtención de índices de vegetación. Estos resultados pueden ser publicados formalmente en una revista científica, o presentados en algún congreso, dependiendo de los resultados.
- A pesar de que se sugieren tres áreas de desarrollo, esto no excluye la posibilidad de explorar otras tecnologías o posibilidades de monitoreo de variables a largo plazo. Esto dependerá de la posibilidad de trabajar con estudiantes de CATIE, que puedan construir instrumentos para sus proyectos. Por ejemplo medir luz dentro del bosque utilizando métodos tradicionales y nuevos sensores electrónicos como estudio comparativo.

## Referencias

Pearce, Joshua M. "Building research equipment with free, open-source hardware." Science 337, no. 6100 (2012): 1303-1304.

Pearce, Joshua M. Open-source lab: how to build your own hardware and reduce research costs. Newnes, 2013.

D’Ausilio, Alessandro. "Arduino: A low-cost multipurpose lab equipment." Behavior research methods 44, no. 2 (2012): 305-313.

Ali, Akram Syed, Zachary Zanzinger, Deion Debose, and Brent Stephens. "Open Source Building Science Sensors (OSBSS): A low-cost Arduino-based platform for long-term indoor environmental data collection." Building and Environment 100 (2016): 114-126.

Hund, Silja V., Mark S. Johnson, and Tom Keddie. "Developing a hydrologic monitoring network in data-scarce regions using open-source arduino dataloggers." Agricultural & Environmental Letters 1, no. 1 (2016).

Hamel, Perrine, Diego Riveros-Iregui, Daniela Ballari, Trevor Browning, Rolando Célleri, David Chandler, Kwok Pan Chun et al. "Watershed services in the humid tropics: Opportunities from recent advances in ecohydrology." Ecohydrology (2017).
Tang, Lina, and Guofan Shao. "Drone remote sensing for forestry research and practices." Journal of Forestry Research 26, no. 4 (2015): 791-797.

Koh, Lian Pin, and Serge A. Wich. "Dawn of drone ecology: low-cost autonomous aerial vehicles for conservation." Tropical Conservation Science 5, no. 2 (2012): 121-132.

Siebert, Sebastian, and Jochen Teizer. "Mobile 3D mapping for surveying earthwork projects using an Unmanned Aerial Vehicle (UAV) system." Automation in Construction 41 (2014): 1-14.

Goodbody, Tristan RH, Nicholas C. Coops, Peter L. Marshall, Piotr Tompalski, and Patrick Crawford. "Unmanned aerial systems for precision forest inventory purposes: A review and case study." The Forestry Chronicle 93, no. 1 (2017): 71-81.

Mohan, Midhun, Carlos Alberto Silva, Carine Klauberg, Prahlad Jat, Glenn Catts, Adrián Cardil, Andrew Thomas Hudak, and Mahendra Dia. "Individual Tree Detection from Unmanned Aerial Vehicle (UAV) Derived Canopy Height Model in an Open Canopy Mixed Conifer Forest." Forests 8, no. 9 (2017): 340.

Ota, Tetsuji, Miyuki Ogawa, Nobuya Mizoue, Keiko Fukumoto, and Shigejiro Yoshida. "Forest Structure Estimation from a UAV-Based Photogrammetric Point Cloud in Managed Temperate Coniferous Forests." Forests 8, no. 9 (2017): 343.

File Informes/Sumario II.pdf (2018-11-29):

## Sumario Proyecto CATIE-FunCR FASE II

Pruebas en sitio de drones y escáner de diámetros y áreas basales

Tomás de Camino Beck, Ph.D.

Sobre este Sumario

Este documento describe el trabajo realizado por el equipo de la Fundación Costa Rica para la Innovación, en la visita a campo realizada el 20 y 21 de setiembre. Este documento sirve de base para mantener registro de lo trabajado, y determinar las acciones a tomar en el desarrollo de los prototipos construidos. Aunque se realizó un análisis preliminar de los datos, el objetivo de esta fase de proyecto no era el análisis de datos, sino solamente explorara la posibilidad de extraer información relevante con los sensores propuestos

Descripción de Actividades

El Viernes 21 y Sábado 22 se viajó a la sede de CATIE en turrialba. En el viaje participaron el Dr. Tomás de Camino, investigador principal, el Dr. Ronnie de Camino, asesor de la Fundación Costa Rica para la Innovación, y Abraham Pineda, experto en drones. De parte del CATIE, participaron Geoffrey Venegas, Juan Jose Serrano y Mariajosé Esquivel, además de algunas personas adicionales de apoyo.

Para el viaje el equipo preparó dos drones de ala fija, adaptaciones para incorporar sensores varios y un LIDAR a el Dron DJI, y un escáner LIDAR con motor rotatorio.

El Viernes en la mañana surgieron varios problemas con el equipo, y se tuvo que reparar algunos aspectos de hardware (cables que no estaba funcionando), y de software (reprogramación de algunos sensores). Una vez reparado los errores, el equipo se dividió en dos grupos: uno para trabajar con el escáner, y el segundo para volar el dron DJI sobre el bosque.

El grupo de escáner trabajó en la subparcela 31, utilizando el escáner LIDAR por 10 minutos, luego procedió a medir la distancia, puntos cardinales y número registrado de árbol, de los árboles de más de 15 cm de diámetros. Se repitió el procedimiento a una distancia de 3 metros del punto original, para tener otro ángulo de visibilidad de árboles. Los datos se registraron de manera digital y escrita.

Zona de Muestreo

En la figura XX se puede observar la zona muestreada. Un bosque secundario con varias parcelas permanentes. La parcela permanente donde se utilizó el escáner LIDAR se muestra en amarillo. Se seleccionó este bosque por la facilidad de acceso, y para asegurar

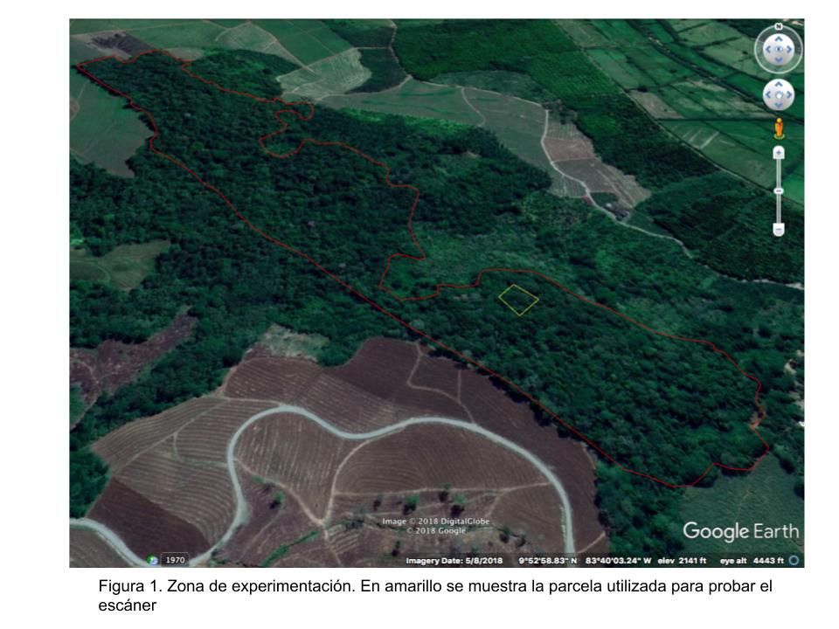
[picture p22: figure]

que en caso de cualquier accidente los drones se puedan recuperar.

El escanéo con Lidar se seleccionó para poder hacer las comparaciones con las medidas de diámetro exactas realizadas en la parcela.

Adicionalmente se realizaron los vuelos con 2 drones de ala fija en el campo principal del CATIE. Esta área facilita realizar vuelos controlados de drones, y permitió validar varios aspectos de diseño de los drones de ala fija.

Vuelos con Dron DJI + LIDAR

Se realizaron en total 10 vuelos con el drone DJI al cual se le conectaron un sensor de presión barométrica, para medir altura, y el LIDAr para medir distancia del dron al suelo. La figura 2 muestra dos de los vuelos por encima del área boscosa.

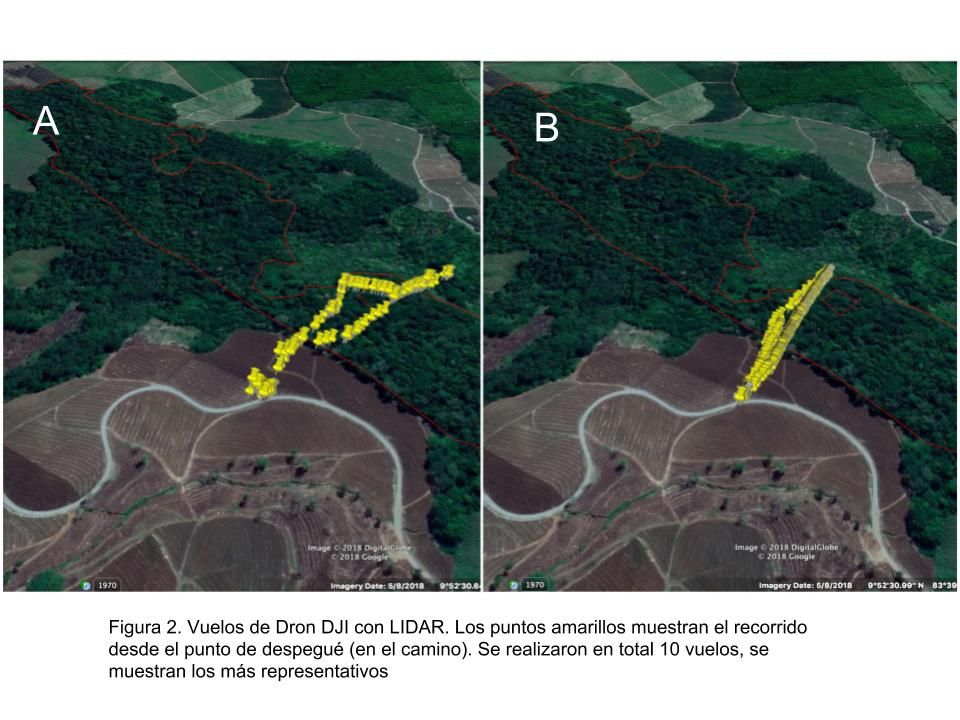
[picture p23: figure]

Los datos recogidos por el Dron se almacenaron en una tarjeta SD. Cada archivo contiene entre 5 mil y 40 mil puntos. Para el análisis de los puntos generados por el Dron, se utilizó Wolfram Mathematica. Se depuraron los datos removiendo información que contenía 0s o duplicaciones, o datos donde el lidar, o el GPS no pudo hacer lectura.

En la Figura 3 se muestran las distancias del dron al dosel del bosque. Los puntos cercanos a 0, son valores donde el dron no pudo obtener la lectura del LIDAR. También se puede observar que la velocidad del dron debe ser baja, para que el lidar pueda hacer la lectura correcta.

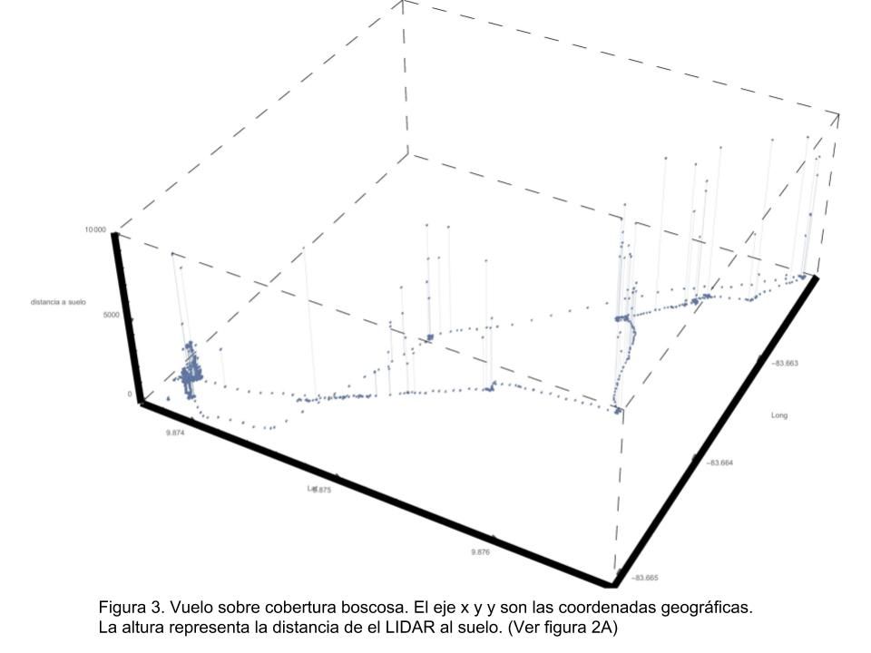
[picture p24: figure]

En la figura 4 se muestran los datos obtenidos en el segundo vuelo realizado. En este vuelo se intentó cruzar el bosque de un lado a otro para analizar los datos y ver si era posible realizar un perfil de altura del bosque.

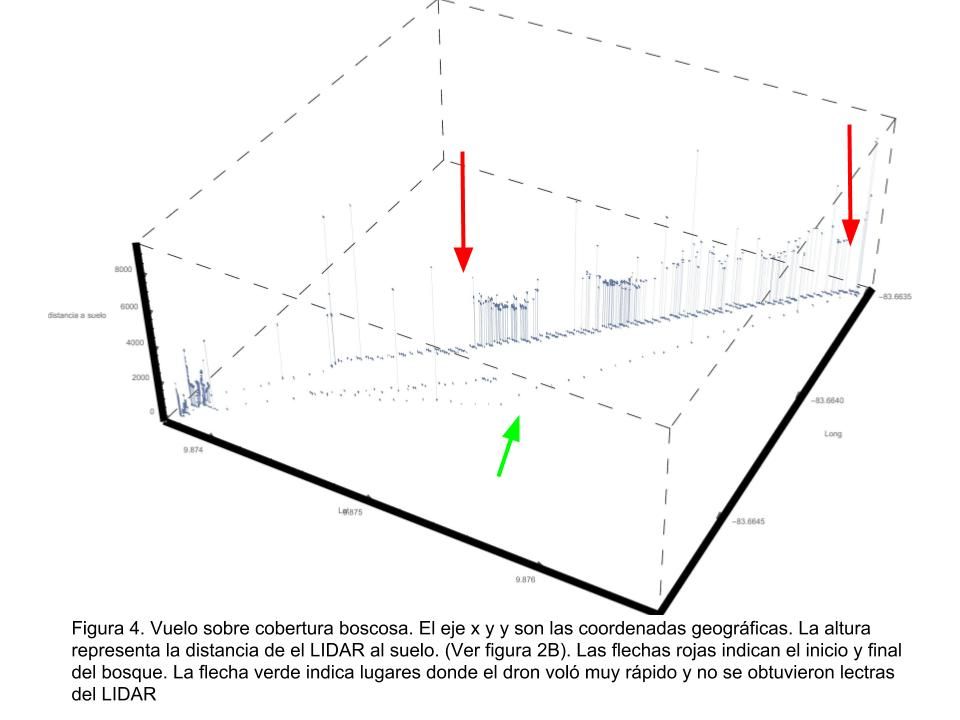
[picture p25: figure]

Resultados principales

- Es posible obtener el promedio y variabilidad de altura de un bosque secundario mediante vuelos de dron
- La facilidad de vuelo y escanéo permite un análisis rápido y frecuente de cambios en la estructura vertical del bosque
- La autonomía de vuelo del dron (6 km o 25 minutos) permite volar una superficie como la del bosquecito probado (el total para hacer un recorrido anda entre los 2km y los 4km)

Cosas por mejorar

- Se debe mejorar el “andamio” para el LIDAR del dron, pues inicialmente, debido a su cercanía con el sensor ultrasónico, el dron tuvo dificultades para poder ser controlado.
- Explorara la posibilidad de que el LIDAR gire
- Determinar los planes y velocidades de vuelo para hacer muestreos

- Se debe encontrar una referencia para la altura del dosel para comparar luego con los datos del LIDAR.
- Falta análisis exhaustivo de los datos

Escáner LIDAR

Para las pruebas, se construyó un escáner con LIDAR con motor giratorio de 270 revoluciones por minuto como se observa en la figura 5.

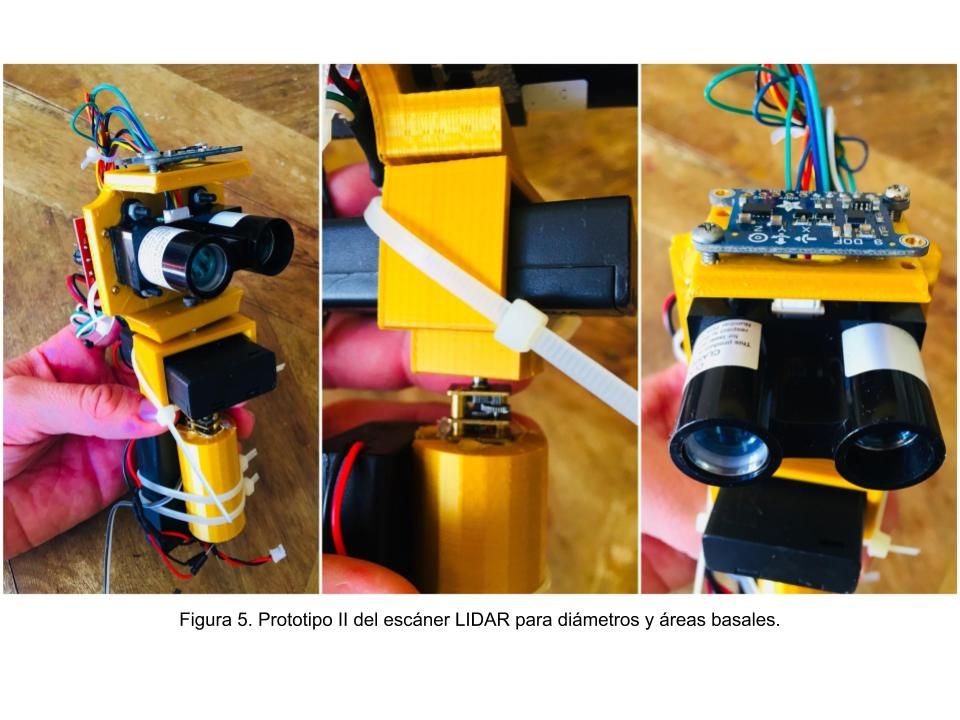
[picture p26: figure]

Se realizaron dos muestras con el escáner LIDAR. Para el muestreo se utilizó un trípode con el LIDAr a 1,30 metros del suelo, y se escanéo por 10 minutos (el escáner toma datos cada 10 milisegundos). Se recogieron los datos con una computadora. Un total de 40 mil puntos fueron registrados. Cada registro contaba con información de punto cardinal (grados con respecto al Norte), y distancia a los árboles.

Una vez hecho el escaneo se procedió a tomar la distancia a los árboles más cercanos (menor a 20 metros), y de diámetros mayores a 15 cm (ver figura 6)


Los datos fueron analizados con Wolfram Mathematica. Se aplicó una metodología de clustering con uso de aprendizaje no supervisado con redes neuronales, para extraer posiciones de árboles con la nube de puntos. La figura 7 muestra los resultados preliminares de las pruebas realizadas.


En la figura se observan los diámetros y posiciones de los árboles según los datos de la parcela permanente, representados como cilindros (el diámetro del cilindro corresponde al diámetro registrado). Existe una alta correspondencia entre los observado en la nube de puntos y los árboles. esto implica que como método de detección de árboles, el LIDAR funciona bien. Se requiere más análisis para determinar si se pueden calcular los diámetros a partir de estos datos.

Resultados principales

- Es posible detectar posición de árboles de forma rápida con escaneo de LIDAR en dos dimensiones
- Los datos se pueden analizar con metodologías de clustering.
- El prototipo mostró funcionar de forma confiable

Cosas por mejorar

- Agregar control de velocidad al Prototipo
- Determinar un protocolo exacto para procesamiento de datos
- Diseñar una versión de el escáner que se pueda manipular con confianza en el campo.

- Cambiar el diseño de rotación (polea o engranaje)
- Mejorar el sistema de montaje sobre el trípode fotográfico
- Determinar una metodología para el análisis de datos para extraer información de diámetros.
- Hacer un muestreo con más parcelas permanentes o una parcela permanente en su totalidad

Vuelo dron autónomo de ala fija

Para pruebas de vuelo de drones de ala fija, se construyeron dos drones como se muestra en la figura 8.


Los drones se probaron en el campo principal del CATIE. Inicialmente se probó aspectos de estabilidad de vuelo y controlabilidad de los drones. También se probaron la funcionalidad de algunos diseños en la estructura.

Se realizaron varios vuelos de prueba. El primero drone sufrió un accidente y cayó en la laguna, lo cual dañó el control de energía del drone. Esto implicó la reconstrucción para un segundo drone de prueba (ver figura 9). El segundo dron voló sin problemas, y su estructura interna impresa en 3D, le dió mucha estabilidad. Sin embargo, debido al peso de la batería, la estructura no soportó y se rompió.


Una vez reparada la estructura interna, se procedió a realizar vuelos autónomos. Se cargó un vuelo sencillo alrededor del campo de CATIE. El vuelo procedió sin problemas y el dron logró hacer vuelos cortos de forma autónoma (sin control remoto). Sin embargo tuvo dificultades en llegar a la altura deseada. Esto pudo haber sido consecuencia de las cortas distancias de vuelo, o de potencia del motor.

Luego de varias pruebas, el ala del dron no soportó la presión de aire y colapso, haciendo que el dron se estrellara. La figura 10 muestra algunas fotos del vuelo (ver video https://youtu.be/Ts5_Yjahy94)


Aunque los drones sufrieron daños en el fuselaje, se recuperó todas las partes electrónicas.

Resultados principales

- Se lograron vuelos estables con el diseño de dron
- El vuelo autónomo es posible en estos drones
- Los drones son fáciles de reparar y permiten adaptaciones sencillas

Cosas por mejorar

- Realizar más pruebas de vuelo autónomo con recorridos más largos y por encima de cobertura boscosa.
- Estructura interna para sensores
- Agregar cámaras con NDVI y GPS
- Incorporar LIDAR

Recomendaciones Finales

1. Para mejorara el dron de ala fija, se debe realizar un trabajo en sitio para ir probando y mejorando el dron de forma rápida. Lo que se propone es realizar un trabajo de unos 5 días en el sitio, con varios drones prefabricados y listos para pruebas. El objetivo de ese trabajo debe ser el vuelo autónomo de drones sobre superficie boscosa
2. Es necesario hacer más pruebas con el el LIDAR montado sobre el DJI. Los resultados indican que es posible determinar estructura vertical del bosque, sin embargo se debe realizar un muestreo completo. Se puede utilizar el mismo bosquecito. Para esto el equipo de CATIE puede realizarlo luego que se les entregue una versión modificada del “Andamio” para que ellos puedan realizar el muestreo con el LIDAR
3. El escáner LIDAR mostró ser funcional. Se deben ahora hacer pruebas de usabilidad y cómo integrarlo en un proceso real de muestreo. Adicionalmente se deben desarrollar las metodologías estadísticas y de manejo de datos para extraer información de diámetros y estructura del rodal.

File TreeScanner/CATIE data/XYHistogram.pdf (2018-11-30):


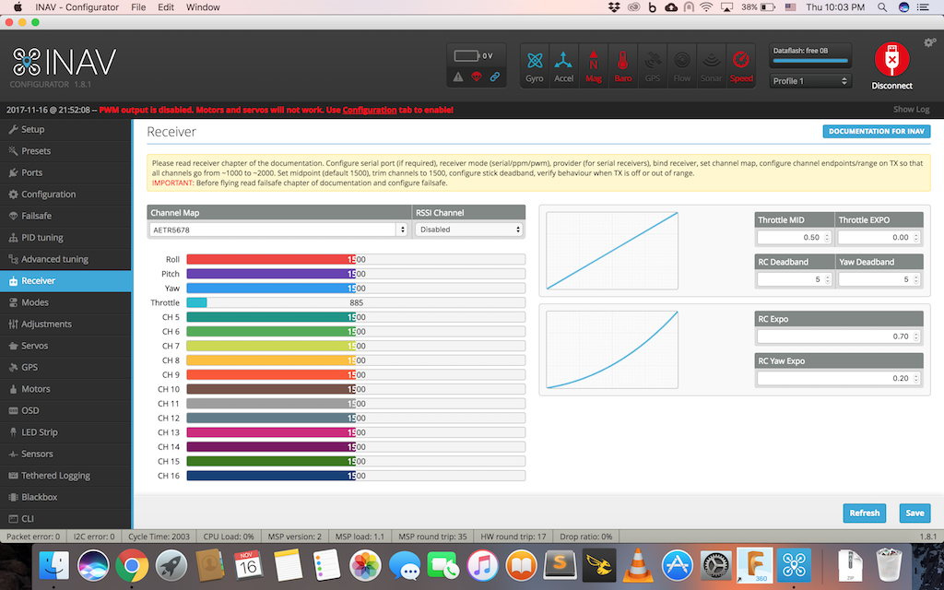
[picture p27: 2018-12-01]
DronAlaFIja/Controlador de vuelo/inav-receiver.png

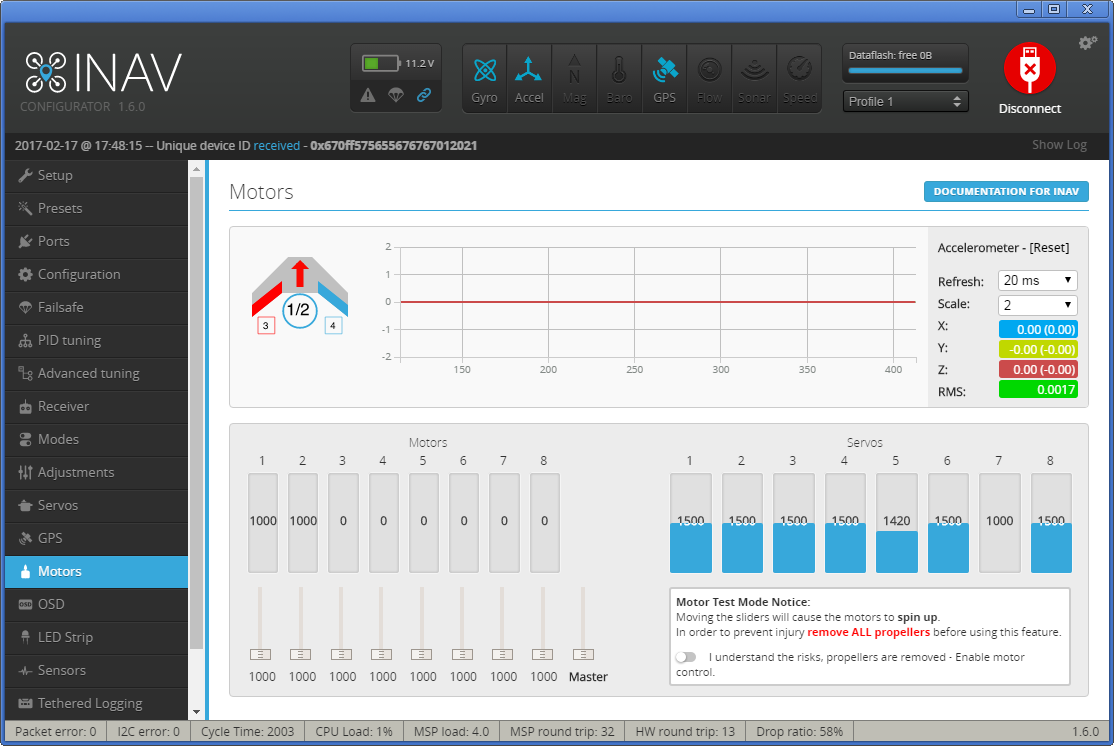
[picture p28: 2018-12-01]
DronAlaFIja/Controlador de vuelo/Inav motores y servos.png

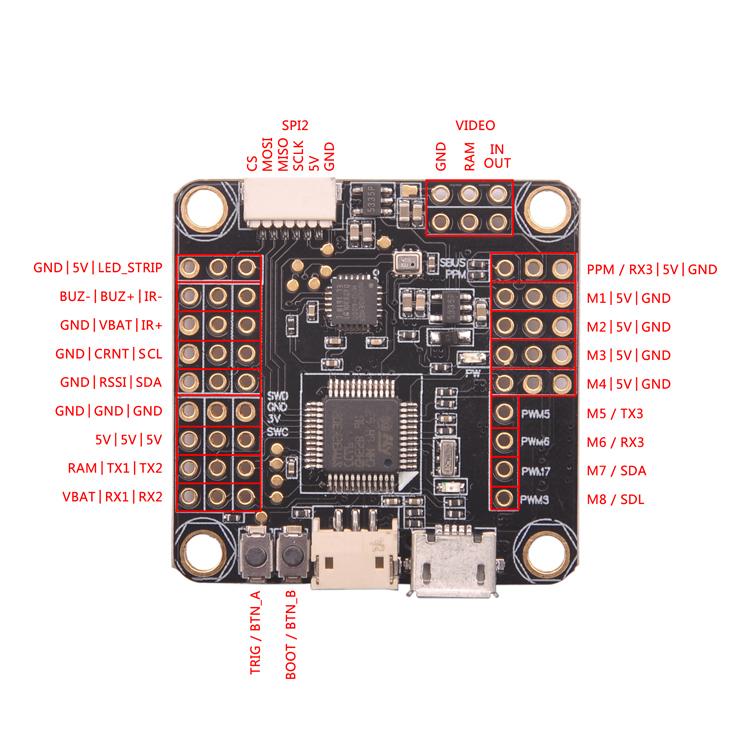
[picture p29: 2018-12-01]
DronAlaFIja/Controlador de vuelo/Inav F3 Diagrama de conexiones.jpg

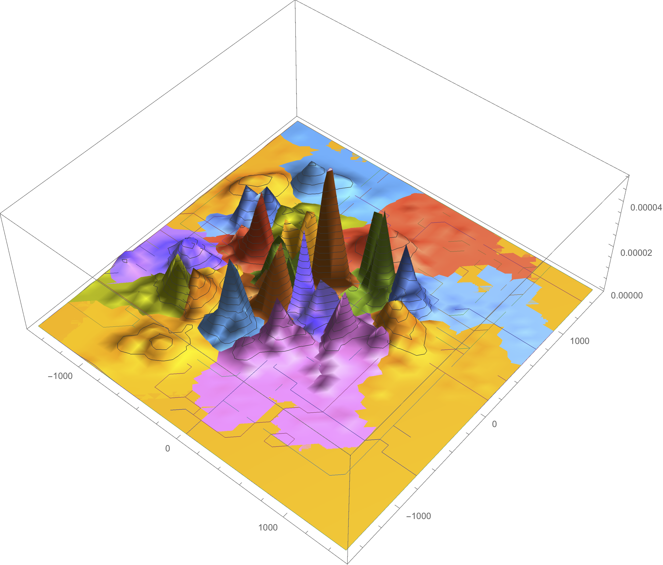
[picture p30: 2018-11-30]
TreeScanner/CATIE data/XYHistogram.png

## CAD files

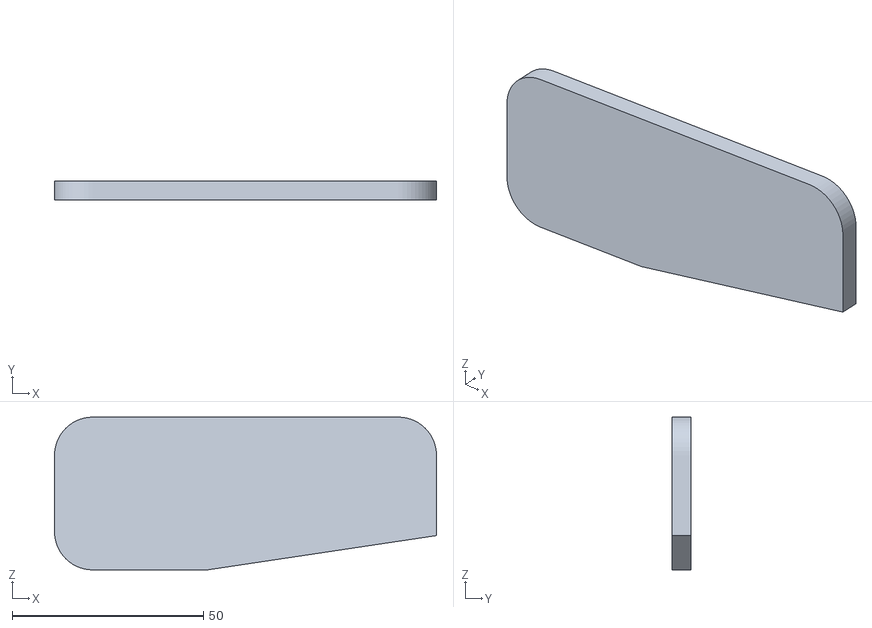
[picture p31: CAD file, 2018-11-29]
DronAlaFIja/FT_spear_wing_angle_tools/files/8.5_asteen_kulmamittari.stl
100.0 x 5.00 x 40.0

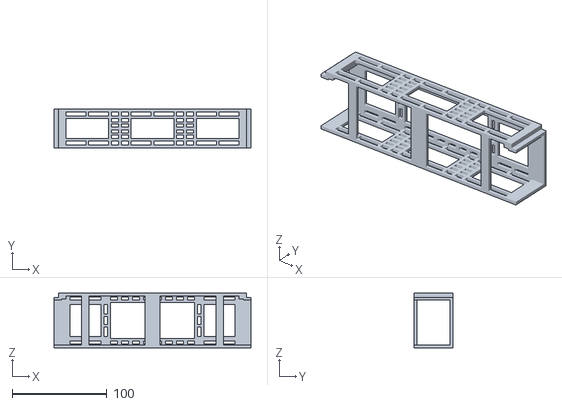
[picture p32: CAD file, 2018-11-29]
DronAlaFIja/MarcoAlaFija/Base central.STL
208.4 x 41.2 x 57.7

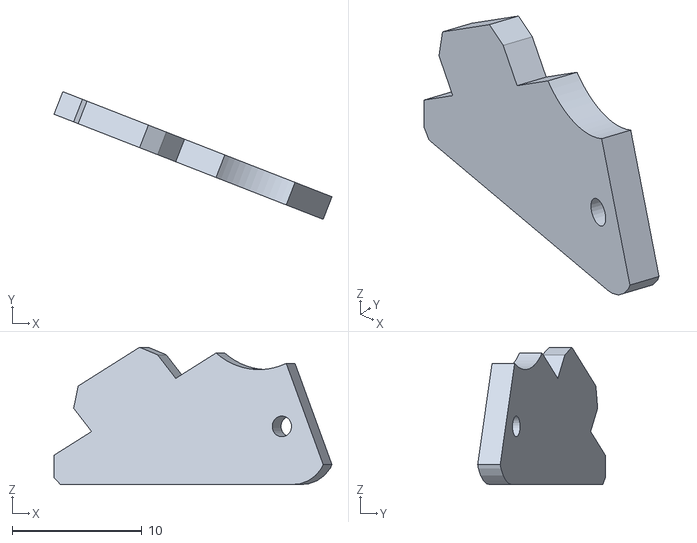
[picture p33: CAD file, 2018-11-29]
DronAlaFIja/OtrasPiezas3D/ft_mini_horn.stl
21.5 x 9.86 x 10.6

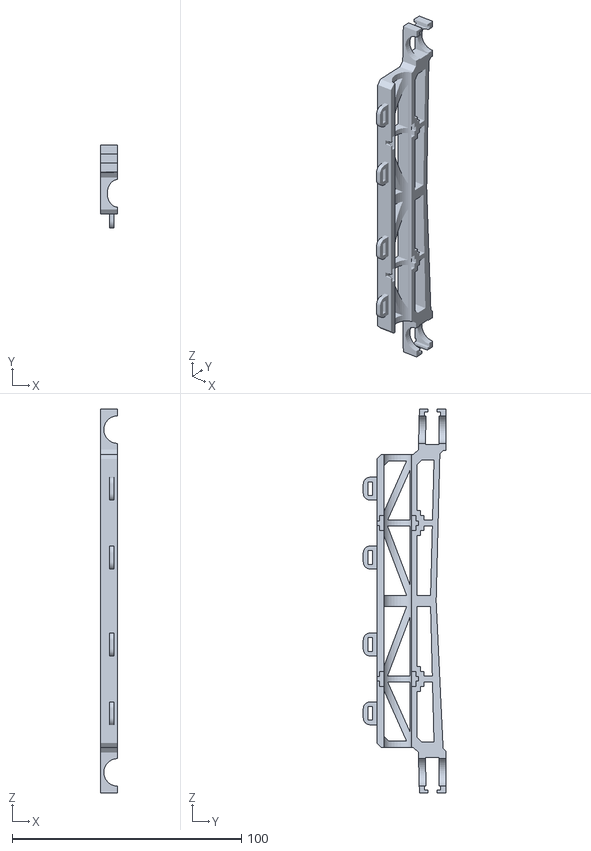
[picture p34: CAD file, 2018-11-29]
QuadLidar/LandingFrame3DFiles/Landing Gear Amarre.STL
7.50 x 36.0 x 167.5

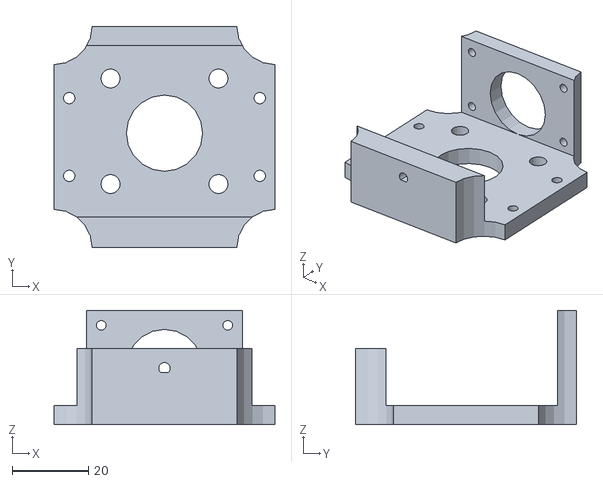
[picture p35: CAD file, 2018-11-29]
TreeScanner/Prototipo1/LIDARbaseS4.stl
58.0 x 58.0 x 30.0

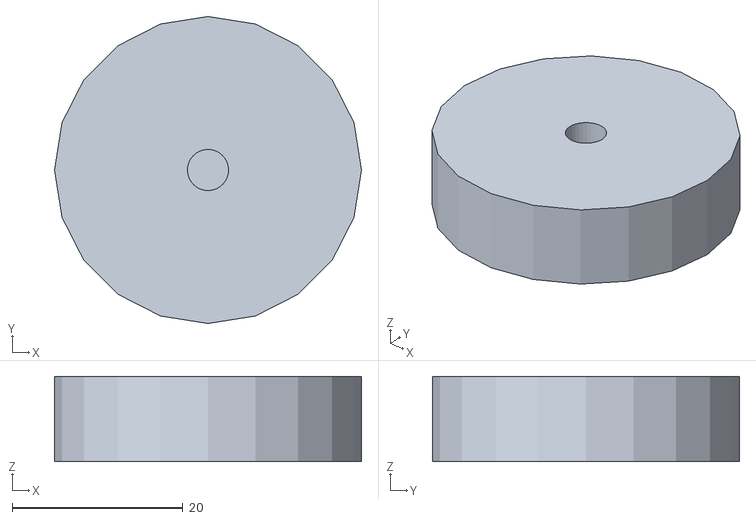
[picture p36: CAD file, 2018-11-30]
TreeScanner/Prototipo2/Rueda_Servo.stl
36.0 x 36.0 x 10.0

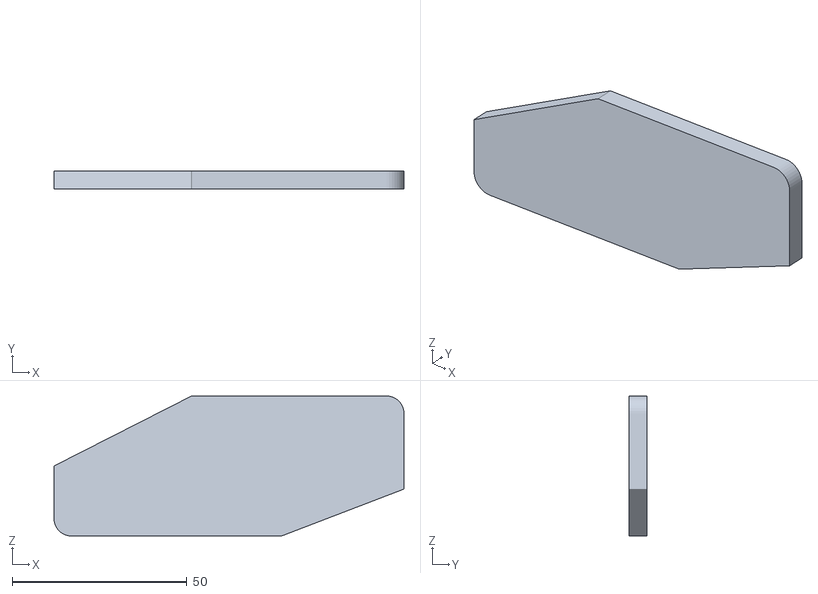
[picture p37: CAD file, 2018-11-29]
DronAlaFIja/FT_spear_wing_angle_tools/files/27_ja_21_kulmamittari.stl
100.0 x 5.00 x 40.0

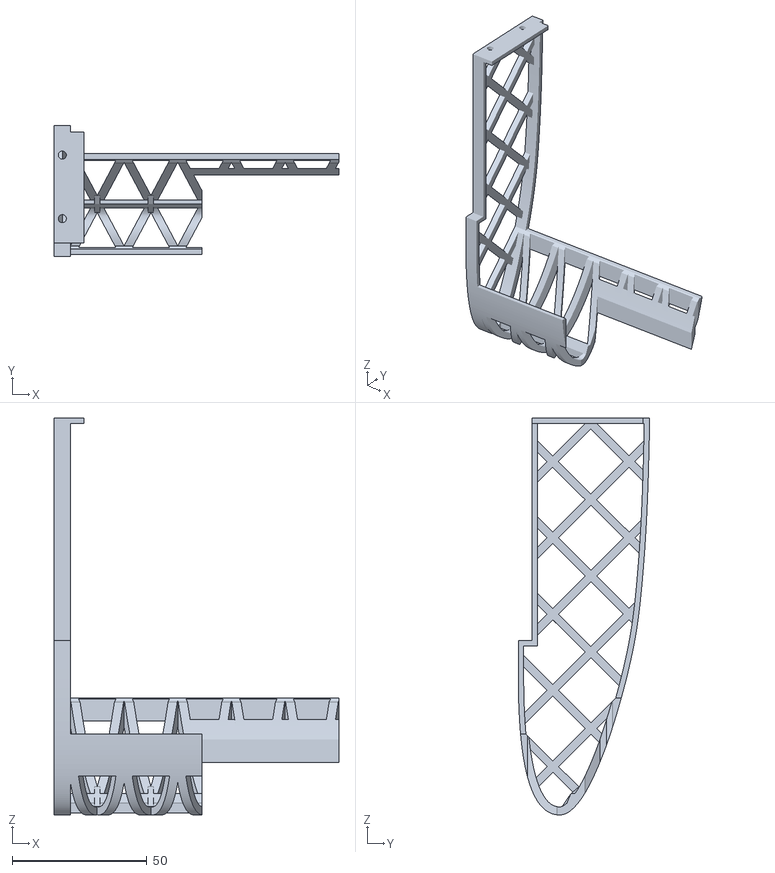
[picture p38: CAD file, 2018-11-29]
DronAlaFIja/MarcoAlaFija/Chasis frente izquierdo.STL
105.5 x 48.7 x 147.2

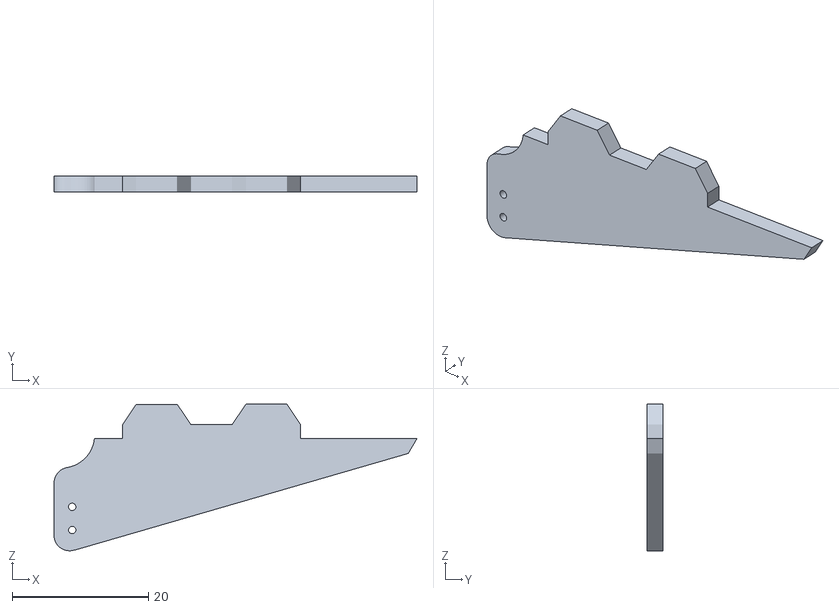
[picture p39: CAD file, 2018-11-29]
DronAlaFIja/OtrasPiezas3D/horn.stl
53.3 x 2.36 x 21.5

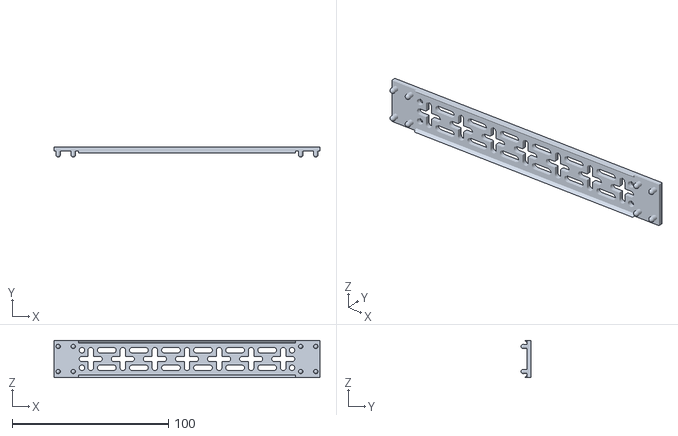
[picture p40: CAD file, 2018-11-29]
QuadLidar/LandingFrame3DFiles/Snap 4.STL
170.0 x 6.47 x 23.8

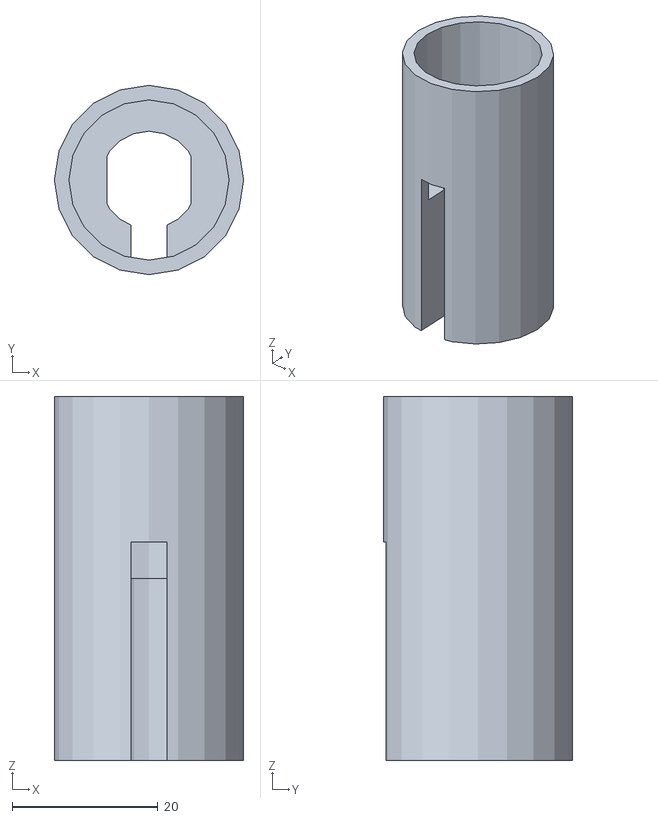
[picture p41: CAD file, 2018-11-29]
TreeScanner/Prototipo1/LIDARJoint2.stl
26.0 x 26.0 x 50.0

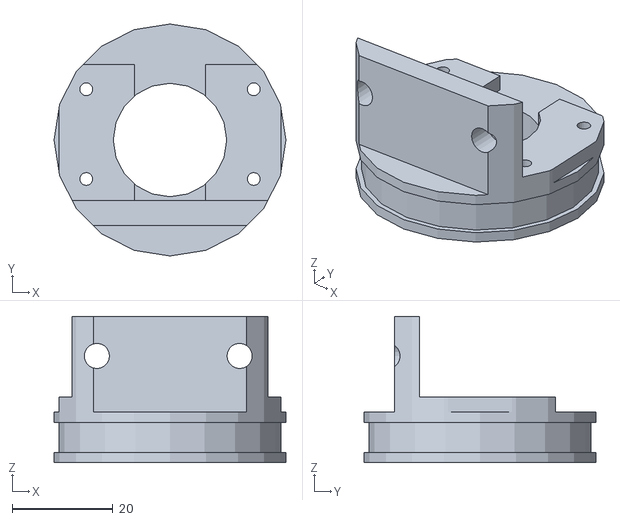
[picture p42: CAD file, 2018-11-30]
TreeScanner/Prototipo2/Base_Lidar_magnetometro.stl
46.0 x 46.0 x 29.0

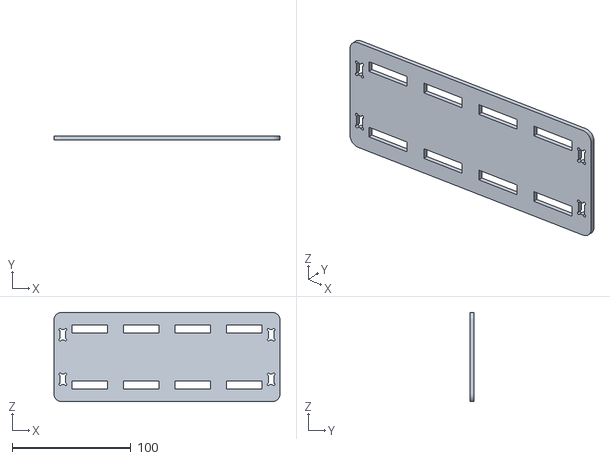
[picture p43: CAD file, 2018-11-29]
DronAlaFIja/MarcoAlaFija/Soporte Baterías.STL
190.0 x 3.00 x 75.0

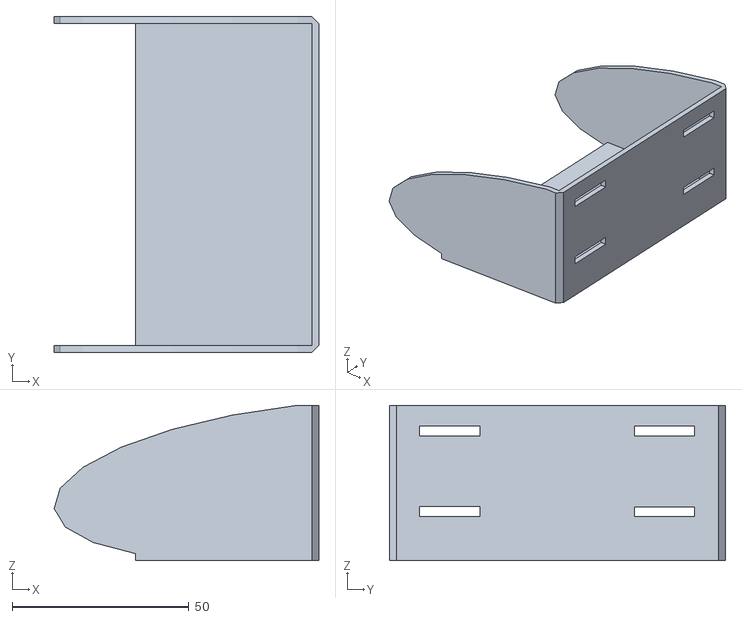
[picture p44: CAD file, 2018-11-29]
DronAlaFIja/OtrasPiezas3D/Cameratray.stl
74.8 x 95.0 x 43.9

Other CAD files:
QuadLidar/LandingFrame3DFiles/Landing Gear Derecho.STL
TreeScanner/Prototipo1/LIDARbase.stl
TreeScanner/Prototipo2/Base_Lidar1.stl
DronAlaFIja/MarcoAlaFija/Chasis atrás izquierdo.STL
DronAlaFIja/MarcoAlaFija/Base snap batería.STL
DronAlaFIja/MarcoAlaFija/Case Motor.STL
DronAlaFIja/MarcoAlaFija/Chasis atrás derecho.STL
DronAlaFIja/MarcoAlaFija/Chasis frente derecho.STL
QuadLidar/LandingFrame3DFiles/Landing Gear Izquierdo.STL
QuadLidar/LandingFrame3DFiles/Snap 3.STL
TreeScanner/Prototipo1/LIDARJoint.stl
TreeScanner/Prototipo1/LIDARJoint3.stl
TreeScanner/Prototipo2/Base_Lidar2.stl

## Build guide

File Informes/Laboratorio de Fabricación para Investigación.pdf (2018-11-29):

# Manual Laboratorio de Fabricación para Investigación

Tomás de Camino BEck, Ph.D.
co-Director de Fundación Costa Rica para la Innovación

# Introducción

Los laboratorios de fabricación (LF) son espacios que permiten la construcción de de cualquier idea o proyecto. Un LF es un espacio equipado con máquinas de fabricación digital, herramientas de mano, materiales de construcción, microcontroladores, computadoras y electrónicos. Este tipo de laboratorios se han desarrollado principalmente en el contexto de educación universitaria y escolar, sin embargo, en los últimos años se han utilizado para el desarrollo de investigación universitaria tecnológica y científica, y en particular para el apoyo en el desarrollo y fabricación de instrumentación científica (Kwok 2017).

Establecer un laboratorio de fabricación es considerablemente mucho más sencillo y directo que otros laboratorios científicos, debido a que las máquinas, hardware y software, es de menor costo, y por que la mayoría de estos instrumentos de Open Source. Esto abre oportunidades para el desarrollo de laboratorios que asistan al investigador o investigadora, a construir instrumentos de medición, que se ajusten a sus necesidades de datos, y no viceversa.

En este manual, detallamos los elementos necesarios, basado en documentación y experiencia propia de la Fundación Costa Rica para la Innovación, para el establecimiento de un laboratorio de fabricación funcional que pueda apoyar el proceso de investigación.

# El Laboratorio de Fabricación

## El espacio

El espacio requerido depende del uso y el objetivo del laboratorio. Se puede considerar como un espacio de aprendizaje, es decir donde se imparten lecciones, un espacio comunitario abierto al público general, y por último un espacio que es un taller de desarrollo de tecnología propia. En ese sentido, lo que se recomienda en cuanto al tamaño (Cavalcanti, 2013),

1. Espacio pequeño de 50 a 250 metros cuadrados. En este puede trabajar de 1 a 10 personas, con espacio adecuado de almacenamiento y requiere poco personal permanente

2. Espacio mediano de enseñanza de 100 a 500 metros cuadrados. En este espacio se pueden dar lecciones, y se tendría suficiente espacio de máquinas y almacenamiento de equipos
3. Espacio grande mayor de 3000 metros cuadrados. Este espacio puede alojar gran cantidad de personas, además de permitir espacio suficiente para pruebas y construcciones de mayor tamaño dentro del espacio

En principio, cualquier espacio se puede convertir en un laboratorio de fabricación, las variables críticas, son la cantidad de personas que espero que puedan estar dentro del laboratorio de manera segura, y el espacio que permita para colocar máquinas, muebles de almacenamiento y mesas de trabajo.

### Distribución

Algunos puntos a considerar:
- La distribución puede variar. Los laboratorios Inventoría de la Fundación Costa Rica para la Innovación, utilizan una distribución con mesas de trabajo con ruedas, y mesas tipo escritorio en la periferia del espacio, con estaciones de trabajo algo más permanente (Figura 1).
- Siempre es importante destinar un espacio para la cortadora láser, que es la máquina que ocupa mayor cantidad de espacio en un laboratorio y que requiere ventilación especial, y con la cual hay que mantener protocolos más estrictos de seguridad. De todas maneras, el espacio depende de el tamaño y potencia de la máquina.
- También es importante destinar una área pequeña para el almacenamiento de materiales, espacialmente materiales para cortado láser, que generalmente son láminas de 120 x 90 cm.
- El distribución puede variar y se recomienda acomodarlo según sea el espacio que se pueda destinar para el laboratorio (en caso que no se construya un espacio dedicado). Una de las características más importantes de estos laboratorios es que son informales y por tanto también deben permitir la organización del espacio según sean las necesidades.

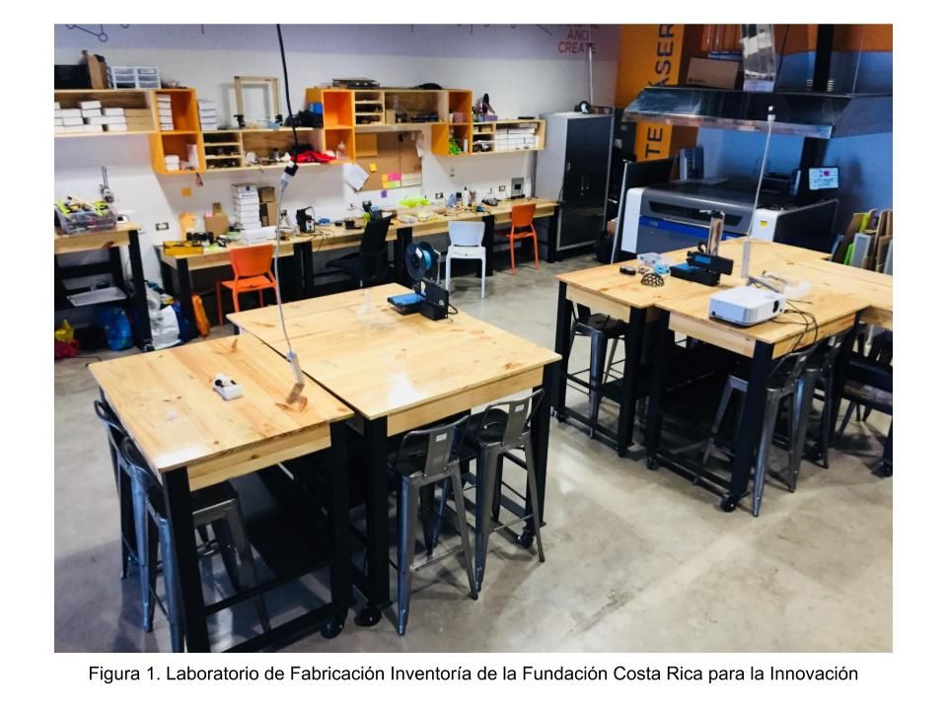
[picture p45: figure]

### Mobiliario

- Mesas de trabajo centrales se recomiendan sean mesas de trabajo de precisión, que permitan soporte de los codos. La altura recomendada está entre 85 a 120 cm. Estas mesas se recomienda tenga ruedas para que puedan ser cambiadas de posición fácilmente en el espacio, para acomodar diferentes usos (Figura 2).
- Mesas de escritorio laterales de dimensiones normales de escritorio
- Todas las mesas de trabajo se recomienda sean de madera cruda, sin ningún tipo de acabado. Estas mesas se espera sufran el maltrato común de un taller de construcción
- Estantería general que permita almacenar materiales y componentes.
- Sillas altas y normales robustas que sirvan para mesas altas y mesas bajas.
- Se recomienda instalar tomas de corriente que provengan del techo del laboratorio, esto facilita movilidad y evita tropiezos en el espacio

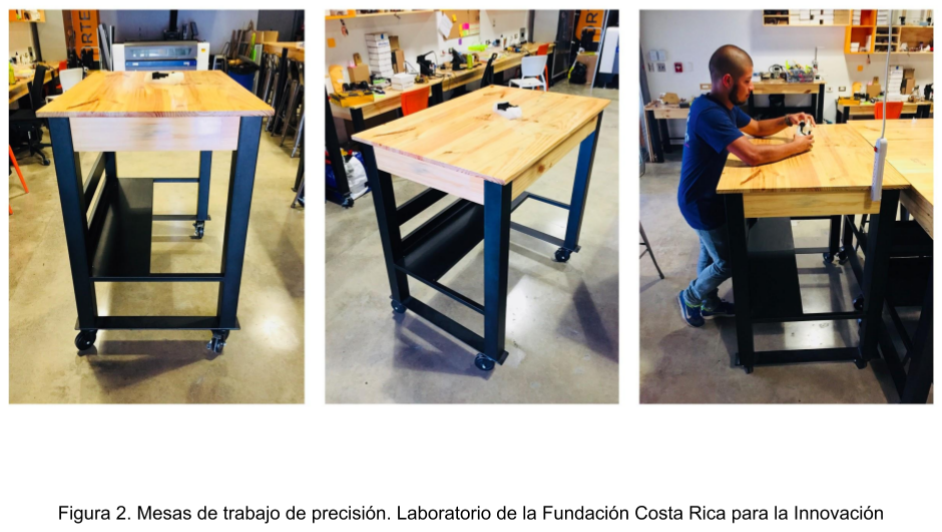
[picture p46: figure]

## Las Máquinas

La máquinas de un laboratorio de fabricación son máquinas de fabricación digital, es decir, toman un archivo digital, y a partir de allí, permiten la construcción de objetos físicos en diferentes materiales.

Basado en experiencia de la Fundación en el desarrollo de laboratorios de fabricación, es de extrema importancia que dichas máquinas sean de naturaleza abierta, es decir, que las máquinas sean Open Source, esto facilita su modificación, adaptación, actualización y reparación, y evita dependencia tecnológica.

En un LF se consideran dos tipos de máquinas, 2D, que construyen en dos dimensiones a partir de un archivo tipo SVG y 3D, que construyen objetos en tres dimensiones a partir de archivos tipo OBJ o STL.

Máquinas 2D

Máquina | Usos | Frecuencia de Uso
Cortadora Láser | Permite cortar materiales como plywood, MDF, acrílico y otros de hasta | Alta

| 1cm de grosor, para la construcción de cualquier tipo de estructuras en dos dimensiones, o piezas de construcciones tri-dimensionales
Fresadora CNC de circuitos | Permite crear circuitos electrónicos. Estos circuitos son necesarios para pruebas para la posterior fabricación de componentes electrónicos | Baja

Máquinas 3D

Máquina | Usos | Frecuencia de Uso
Impresora 3D | Construcción aditiva a partir de materiales plásticos varios como, PLA, ABS, Nylon, Latex, silicona, etc. Las impresoras permiten la fabricación de objetos tridimensionales a partir de diseños 3D | Alta
Fresadora CNC | Construcción sbstractiva a partir de gastar material con una broca. Se puede trabajar en Madera, plasticos, Aluminio, y cualquier material que se puede trabajar con brocas | Baja

## Herramientas de mano y electrónicas

Las herramientas de mano son vitales para poder facilitar la construcción. Estas por lo general son de bajo costo y se pueden adquirir fácilmente en el mercado. Estas incluyen:

1. Destornilladores variados
2. Destornilladores pequeños
3. Taladro de precision (Dremel o similar)
4. Taladro
5. Caladora de Madera
6. CIntas metricas varias

7. Escuadras y reglas de madera y/o metal
8. Prensa de taladro
9. Prensas varias
10. Cautin
11. Cautin de aire caliente
12. Multímetro
13. Alicates varios
14. Sierra
15. Martillos de goma y normales
16. Prensa para electrónicos
17. Tercera mano (prensa para soldar)
18. soplete pequeño
19. Fuente de poder variable

## Electrónicos

Los electrónicos se dividen en sensores y actuadores. En los sensores, se incluyen componentes electrónicos adicionales para prototipado

### Los sensores

Sensor | Uso
Pantalla OLED | Pantalla para despliegue de datos en controladores
Sensores de temperatura | Medición de temperatura
Sensores de Luz de alto rango | medir luz visible, ultravioleta e infrarroja
GPS | Geo-localizción
Amplificadores de ganancia para sensores | Amplificar información de sensores analógicos de baja ganancia
Sensor de presión atmosférica, temperatura y humedad | Para medición de altura sobre nivel del mar y otras variable atmosféricas
Sensor elástico de conductividad | Medir deformaciones
Sensor de llamas | Detección de llamas
Sensor de tacto | Interruptores de tacto
Sensor de temperatura superficial | Mide temperatura de superficie de objetos de manera rápida
Sensor de flujo de líquidos | Mide flujos de agua en una tubería
Sensor de Carga (peso) | Detectar peso y carga
Sensor de polvo | Detecta partículas en suspensión en el aire, desde neblina, hasta polvo

Sensor de presión y tacto | Plástico que permite detectar deformaciones
Sensor humedad de suelo | Mide humedad (conductividad) del suelo
Sensor de temperatura industrial | Soporta rangos amplios de temperatura
Sensor de gotas de agua | Sensor que determina humedad en superficie
Termocupla para sensores de temperatura | Adaptador para sensor industrial de temperatura
Estaciones meteorológicas portátiles | Estaciones de bajo costo para variables atmosféricas
Sensor de 9 grados de libertad (giroscopio, acelerómetro y magnetómetro) | Para navegación y posicionamiento espacial
Breadboards de prototipado | Para desarrollo rápido de prototipos electrónicos
Cables jumper de prototipado (m-m,m-f,f-f) | Cables para el breadboard
Cargador baterías LiPo | Cargador de baterías para proyectos
Kit de resistencias, capacitores, transistores | Para desarrollo de circuitos eléctricos

### Actuadores

Tipo | Uso
Motor DC | Motores de corriente directa
Servo motor | Motores de rotación definida
Motores de paso (stepper) | Motores de movimiento controlados
Leds varios | Luces LED, neo-pixeles y de color fijo

### Microcontroladores

Los microcontroladores son pequeñas computadoras que permiten conectar sensores, obtener información de ellos y poner a funcionar actuadores. Son computadoras de propósito general de bajo consumo de energía y programables.

Controlador | Usos
Arduino UNO | Placa básica de prototipado para enseñanza y pruebas
Feather M0 | Placa de prototipado con controlador M0
Feather Addalogger | Placa de prototipado para sistemas de datalogger
Feather LoRa | Placa de Prototipado con conexión de Radio de largo

| alcance
Feather FONA | Placa de prototipado con conectividad celular para aplicaciones IoT

### El Software

Se lista el software que normalmente se utiliza. Se busca software de acceso libre para bajar costos de operación, y para facilitar compartir información.

Software | Tipo De LIcencia | Usos
Tinkercad.com | Libre en línea | Introducción al diseño 3D, preparación de diseños 3D para impresión.
Fusión 360 | Libre de uso limitado | Desarrollo de diseños 3D avanzados
InkScape | Libre | Diseño 2D, preparación de archivos para corte laser
Arduino IDE | Libre | Programación de microcontroladores
Processing | Libre | Desarrollo de interfaz, y prototipado de software
Google Sheets | Libre | Manejo de datos

# Recomendaciones Generales

- Esta lista de materiales son recomendados para un laboratorio de fabricación, sin embargo, de acuerdo a necesidades, esta lista puede aumentar o disminuir. La mayoría de laboratorios contiene una o varios de los componentes sugeridos, dependiendo del uso.
- Muchos componente se van adquiriendo en base a proyectos, sin embargo el contar con una existencia de componentes, facilita el desarrollo y prueba rápida de ideas, y la construcción rápida de soluciones para fabricación.

# Lista de Materiales Ya adquiridos

Raspberry Pi High-Precision 24bit AD/DA Expansion Board CRCibernética Raspberry Pi 3 Starter Kit
Feather M0 Datalogger

FeatherWing OLED - 128x32 OLED Add-on For All Feather Boards Lithium Ion Polymer Battery - 3.7v 1200mAh
SONOFF TH Sensor - DS18B20
Adafruit TSL2591 High Dynamic Range Digital Light Sensor Adafruit Ultimate GPS Breakout - 66 channel w/10 Hz updates ADS1115 16-Bit ADC - 4 Channel with Programmable Gain Amplifier
Atmospheric Sensor Breakout - BME280
Conductive Rubber Cord Stretch Sensor + extras!
Flame Sensor Module
Human Body Touch Sensor
Infrared Thermometer - MLX90614 Liquid Flow Meter 3/4 inch - BRASS Load Cell - 10kg, Straight Bar (TAL220) Load Cell Amplifier - HX711
Optical Dust Sensor - GP2Y1010AU0F Pressure-Sensitive Conductive Sheet (Velostat/Linqstat) Soil Humidity Sensor (Hygrometer)
Temperature Sensor with Steel Head
Raindrop and Dew Sensor
Thermocouple Amplifier with 1-Wire Breakout Board - MAX31850K Weather Meters
Adafruit 9-DOF IMU Breakout - L3GD20H + LSM303
Original PRUSA i3 MK2S 3D Printer (Assembled) Clear Breadboard (8.3 x 5.5 cm)
40pin 20cm Jumper Wire Male to Male
Female to Female Jumper Wire
Male to Female Jumper Wire
LiPo Charger Basic - Micro-USB

Requerimientos

Para poder indicar cantidades debe definirse primero el espacio para definir la capacidad máxima y la afluencia de personas y proyectos. Ya se llevó a cabo una visita y se valoraron dos espacios. Una vez definido el espacio se hará la recomendación y el proceso de gestión e implementación del laboratorio de fabricación.

Referencias

Kwok, R. (2017). Field instruments: Build it yourself. Nature, 545(7653), 253-255.

Lesteiro-Tejeda, J. A., Hernández-Delfín, D., & Batista-Leyva, A. J. (2017). Automation of Experiments using Arduino. Revista Cubana de Física, 34(2), 120-124.

Cavalcanti, G. (2013). Making Makerspaces: Creating a Business Model. Make: DIY Projects, How-Tos, Electronics, Crafts and Ideas for Makers, 4.

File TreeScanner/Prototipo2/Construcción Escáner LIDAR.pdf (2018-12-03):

# Construcción Escáner LIDAR

Tomás de Camino Beck, Ph.D.

## Introducción

El escáner LIDAr es un escáner de lecturas del sensor de distancia láser de alta resolución. El escáner rota 360 grados haciendo lecturas de distancia cada ciertos intervalos, y registrando el ángulo con respecto al norte magnético. La distancia máxima de lectura del LIDAR es de 50 metros.

La función del escáner es detectar una nube de puntos para luego determinar la presencia de árboles en un rodal, y posteriormente calcular diámetros y áreas basales. este dispositivo se encuentra en fase de prototipo, por tanto es necesario realizar ensayos de campo para validar su funcionamiento.

## Materiales

- Rol genérico de patineta
- Microcontrolador (en este documento se utiliza un S4A)
- Servomotor de rotación contínua
- Extensiones (stand off)
- Slip ring de 6 cables
- LIDAR lite
- ADAfruit 9DOF
- Impresora 3D
- Taco anclaje metal 1/2"
- Elásticos varios

## Impresión 3D

Imprimir en impresora 3D en resolución de 300 micras (0.3mm) las piezas del siguiente repositorio GitHub, (https://github.com/FunCR/ProyectoCATIE/tree/master/TreeScanner/Prototipo2) como se ve en la fotos.

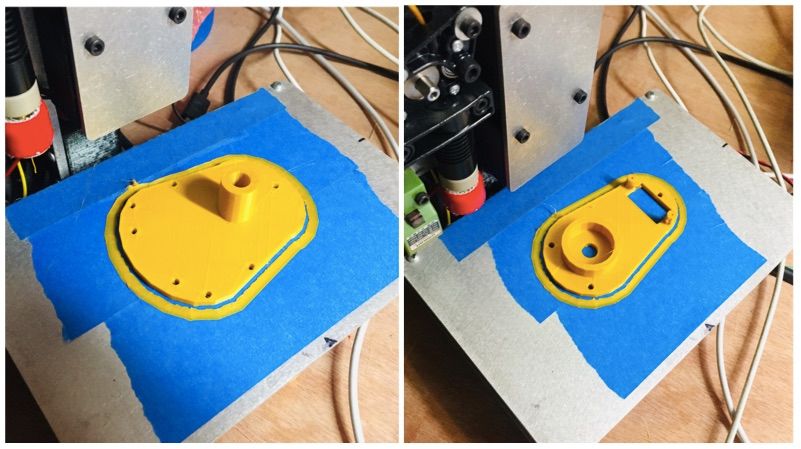
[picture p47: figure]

Para la impresión del prototipo se utilizó plástico PLA, con una impresora Printrbot Smalls.

## Ensamblado de la base

Colocar el microcontrolador y fijarlo con tornillos a la base impresa en 3D. Colocar las extensiones. En este caso se utilizan extensiones de 2cm y una adicional de 6mm. (ver fotos)

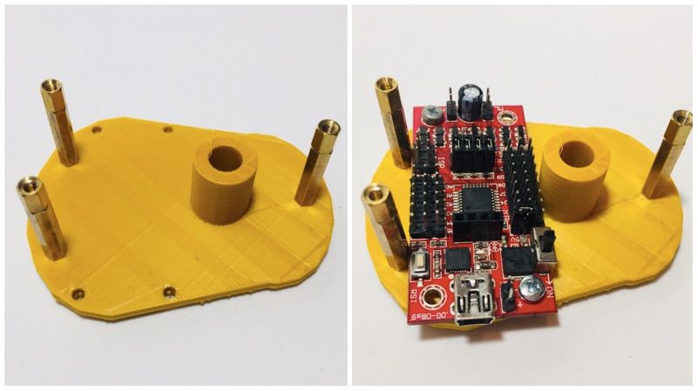
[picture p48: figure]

Importante colocar el anclaje de metal. El anclaje permite luego utilizar un trípode fotográfico para fijar el escáner. En la siguiente foto se muestra cómo colocarlo

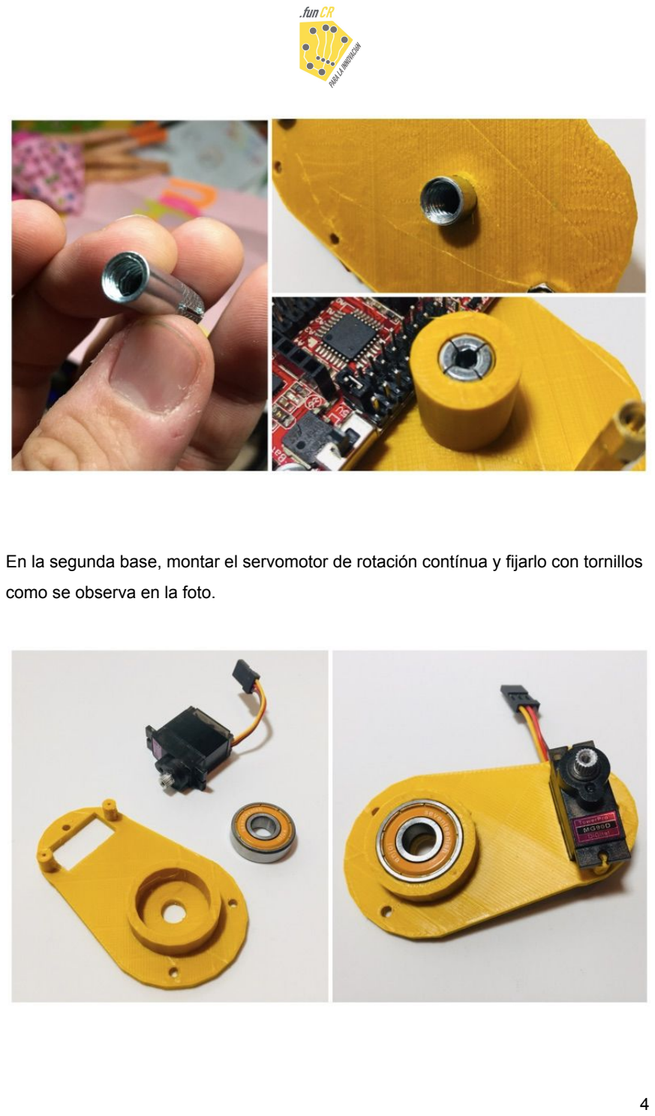
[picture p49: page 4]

En la segunda base, montar el servomotor de rotación contínua y fijarlo con tornillos como se observa en la foto.

Una vez que las dos bases estén ensambladas, atornillar la base superior a la inferior como se muestra en la siguiente foto

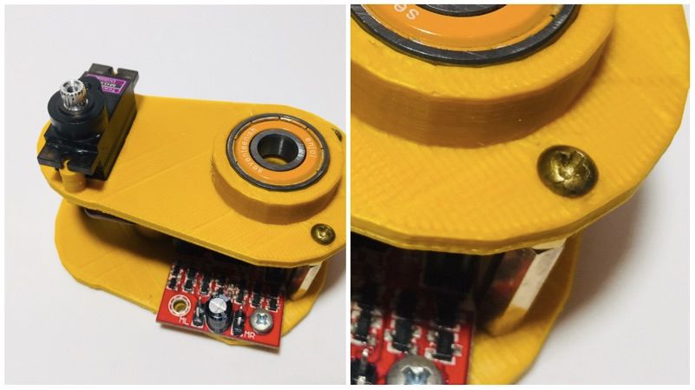
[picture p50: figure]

## Ensamblado del Lidar y magnetómetro

El LIDAR y el magnetómetro van colocados sobre el “slip ring” que permite la rotación de cables y que ambos sensores se muevan libremente. Ambos sensores se colocan sobre la pieza impresa de PLA como se ve en el siguiente esquema

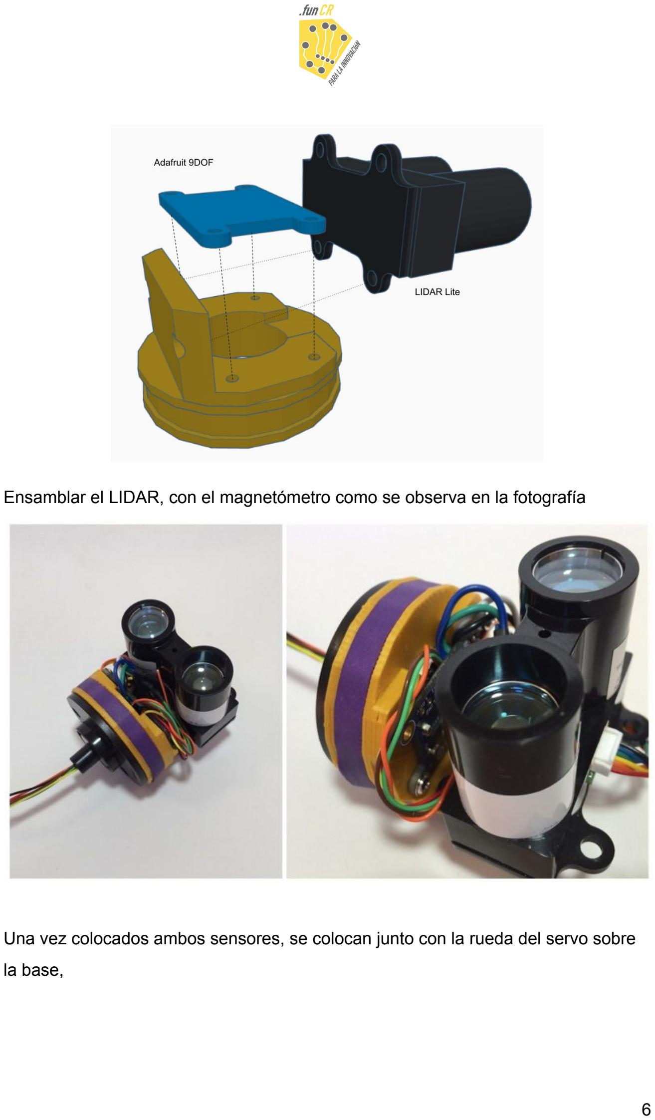
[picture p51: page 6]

Ensamblar el LIDAR, con el magnetómetro como se observa en la fotografía

Una vez colocados ambos sensores, se colocan junto con la rueda del servo sobre la base,

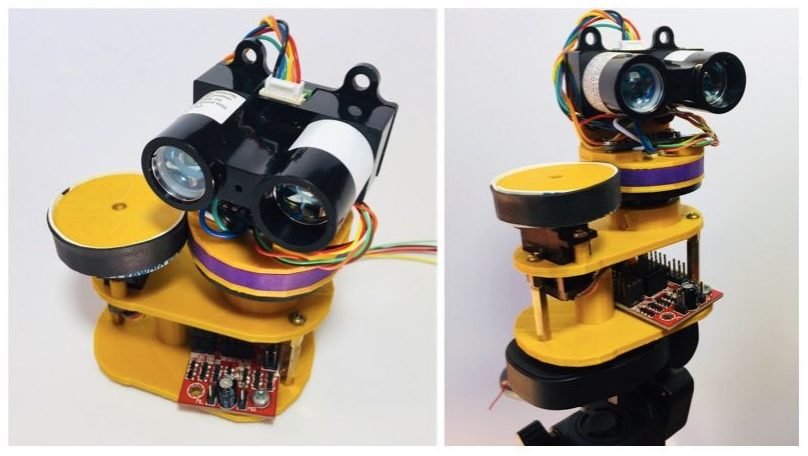
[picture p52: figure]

## Hardware y código

El hardware se conecta de manera bastante simple. Las conexiones SDA, SCL, del LIDAR van conectadas directamente con las conexiones SDA y SCL del magnetómetro 9DOF. De igual manera las conexiones de GND y 3V. Estas se conectan a los cables de “Slip Ring”, y de allí a las conexiones de SDA (A4) y SCL (A5) del controlador S4A. El servomotor se conecta directamente al S4A en el pin número 9, pero la alimentación de poder se conecta a ML en el S4A. El esquema de conexión se puede ver en el siguiente esquema

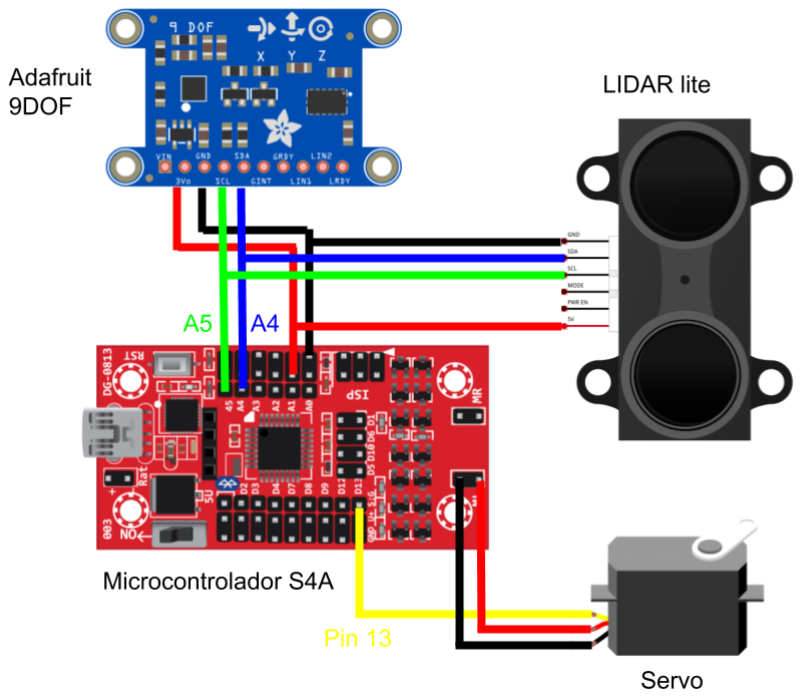
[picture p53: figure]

El código se encuentra en el ANEXO, o en el siguiente repositorio de GitHub .

1

## Operación

Colocar el escáner sobre el trípode

1 https://github.com/FunCR/ProyectoCATIE/tree/master/TreeScanner/Code

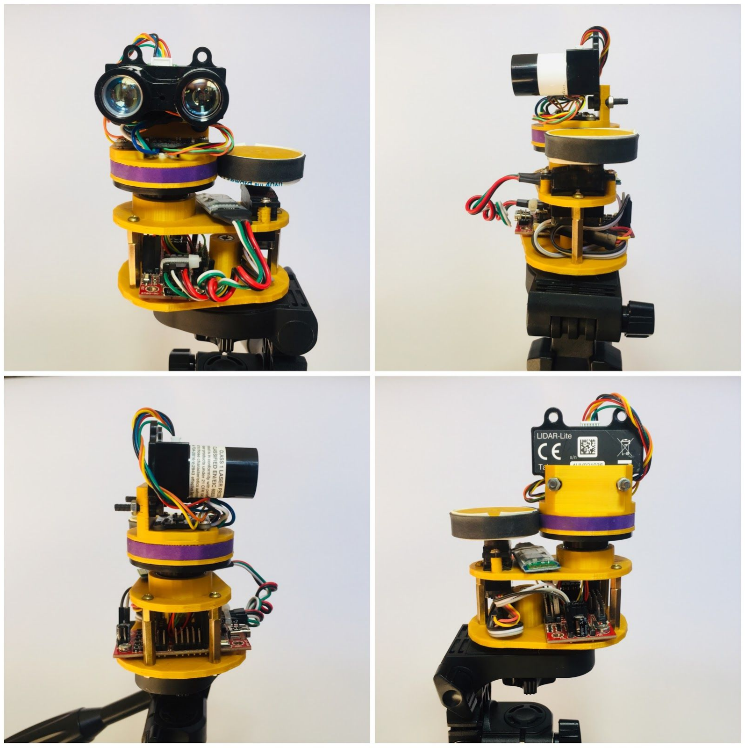
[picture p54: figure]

- Conectar el puerto USB del escáner a la computadora. El escáner comenzará a rotar y a tomar datos de forma inmediata. Para ver los datos, abrir el Arduino IDE, y abrir el monitor serial.
- Los datos son arrojados por el escáner en conexión serial a 9600 Baudios. Los datos se leen en formato “ángulo (grados), distancia (en cm)”. El ángulo es la lectura del magnetómetro que corresponde a los grados con respecto al norte magnético.
- El escáner se debe dejar leyenda por varios minutos para que recoja una “nube” de puntos suficientemente densa, para luego detectar la presencia de árboles en un rodal. El LIDAR hace una lectura de 1, cuando no puede determinar la distancia.
- Los datos recogidos en la terminal serial del Arduino IDE, se puede copiar y pegar en un archivo de texto (sin formato), para luego se procesados (recomendado)
- Del mismo modo, se puede leer los datos de forma visual a través del Lidar Viewer, que se desarrolló como parte de este proyecto y que corre en la plataforma Processing.org.

# LIDAR Viewer

Tomás de Camino Beck, Ph.D.

## Introducción

Lidar viewer es el prototipo de un visualizador de datos del escáner LIDAR. El software se desarrolló en Processing.org una platforma de código abierto que permite el desarrollo de prototipos de software rápidamente, con códigos escritos en JAVA. Esta plataforma además permite ir modificando el código y distribuyendolo en forma rápida, pues corre de manera transparente en cualquier versión instalada de Processing.

El LIDAR Viewer, permite la visualización de datos crudos del escáner LIDAR, pero además implementa un algoritmo de agregación que permite identificar estructuras constantes en el escanéo. En el caso de esta aplicación, permite la identificación de árboles. A partir de identificar las estructuras o árboles, es necesario una investigación para establecer la relación entre puntos de borde de estructuras y estimación de diámetro.

El software se conecta al Escáner LIDAR a través del puerto serial con un módulo Bluetooth 2.0 que se encuentra en el escáner. Sin embargo también es posible visualizar los datos a través de cable USB

El código se encuentra en prototipo, y está sujeta a cambios. El código para correr en Processing, se puede descargar en el repositorio GitHub (Se adjunta como ANEXO).

2

## Recepción de datos

Los datos son recibidos por el LiDAR Viewer, como tuplas de datos,

2
https://github.com/FunCR/ProyectoCATIE/blob/master/TreeScanner/Code/LIDAR_Viewer/LIDAR_Vie wer.pde (https://github.com/FunCR/ProyectoCATIE/blob/master/TreeScanner/Code/LIDAR_Viewer/LIDAR_Viewer.pde)

Una nube de puntos lo constituye un conjunto grande de puntos ángulo distancia. Mediante esta nube de puntos es posible reconstruir información espacial en 2 dimensiones.

Cada 50 milisegundos el software recibe los datos. estos datos se pueden visualizar crudos (toda la nube de puntos) o como agregados de datos

## Algoritmo

La meta del algoritmo es crear “clusters” de puntos para identificar estructuras permanentes (árboles). La estrategia para lograrlo es agrupar los puntos por proximidad espacial, es decir, se asume que cuando un fuste es detectado, existirá un grupo de puntos muy cercanos, con los bordes marcados por puntos distantes.

Los valores ángulo distancia se convierten a coordenadas cartesianas mediante las siguientes fórmulas,

Cada par ordenado x,y representa un punto pi

. La distancia entre dos puntos se calcula mediante la distancia euclidiana definida como,

Donde p1

y p2

representan dos puntos cualesquiera en la nube de puntos. COnsideremos el siguiente conjunto de datos agrupados,

Donde x y y son un promedio de puntos dentro de un rango de distancia predeterminado (centroide), y c es el conteo de puntos con ese centroide. Las estructuras predominantes o más “sólidas” tendrán un conteo de puntos más alto. Al escanear un bosque, los troncos de árboles serán estructuras predominantes.

El pseudocódigo del algoritmo es el siguiente,

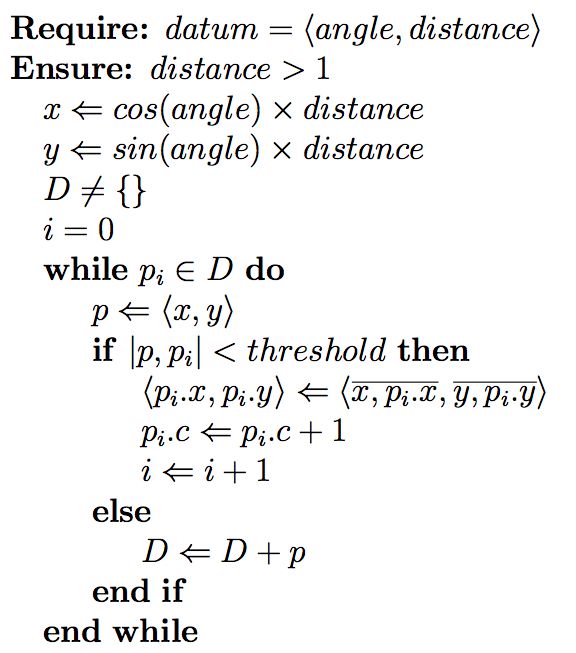
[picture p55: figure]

El código completo en JAVA se puede ver en el ANEXO.

## Utilización

1. Se debe instalar Processing. Para hacerlo, descargar e instalar el programa en el sitio de Processing.org³
2. Descargar el código del repositorio de GitHub .

4
3. EN processing, abrir el código de Lidar_Viever.

3https://processing.org/
4 https://github.com/FunCR/ProyectoCATIE/tree/master/TreeScanner/Code/LIDAR_Viewer

4. En la línea String portname = "/dev/tty.HC-06-DevB"; el valor "/dev/tty.HC-06-DevB" indica el nmbre del puerto a donde se encuentra el bluetooh. Este se indica una vez que hayan hecho el “pairing” con el buetooth “HC-06” del escáner Lidar.
5. Una vez que se aseguren que el Bluetooth está registrado en la computadora, presionar el botón de play en processing.

## Interfaz

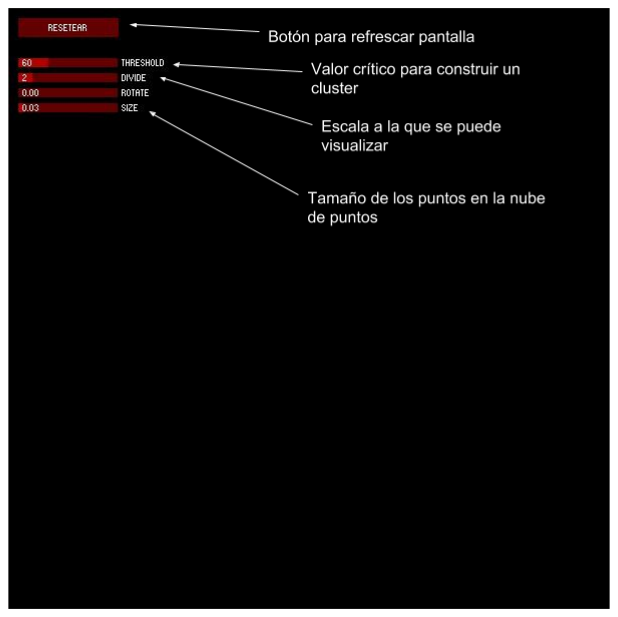
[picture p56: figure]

UNa vez hecha la conexión con el USB, el programa comenzará a despegar la nube de puntos. Los puntos de un cluster, se verán como círculos cada vez más grandes. El tamaño de esos circulos de puede cambiar con el slider etiquetado “SIZE”. Si se mueve el slider “THRESHOLD” se puede cambiar la tolerancia de la distancia euclidiana para formar los clusters.

El Slider “DIVIDE” simplemente es la escala a la cual despliega los puntos, y el botón “RESETEAR” permite refrescar la pantalla.

Luego de algunos minutos la pantalla se verá de la siguiente manera,

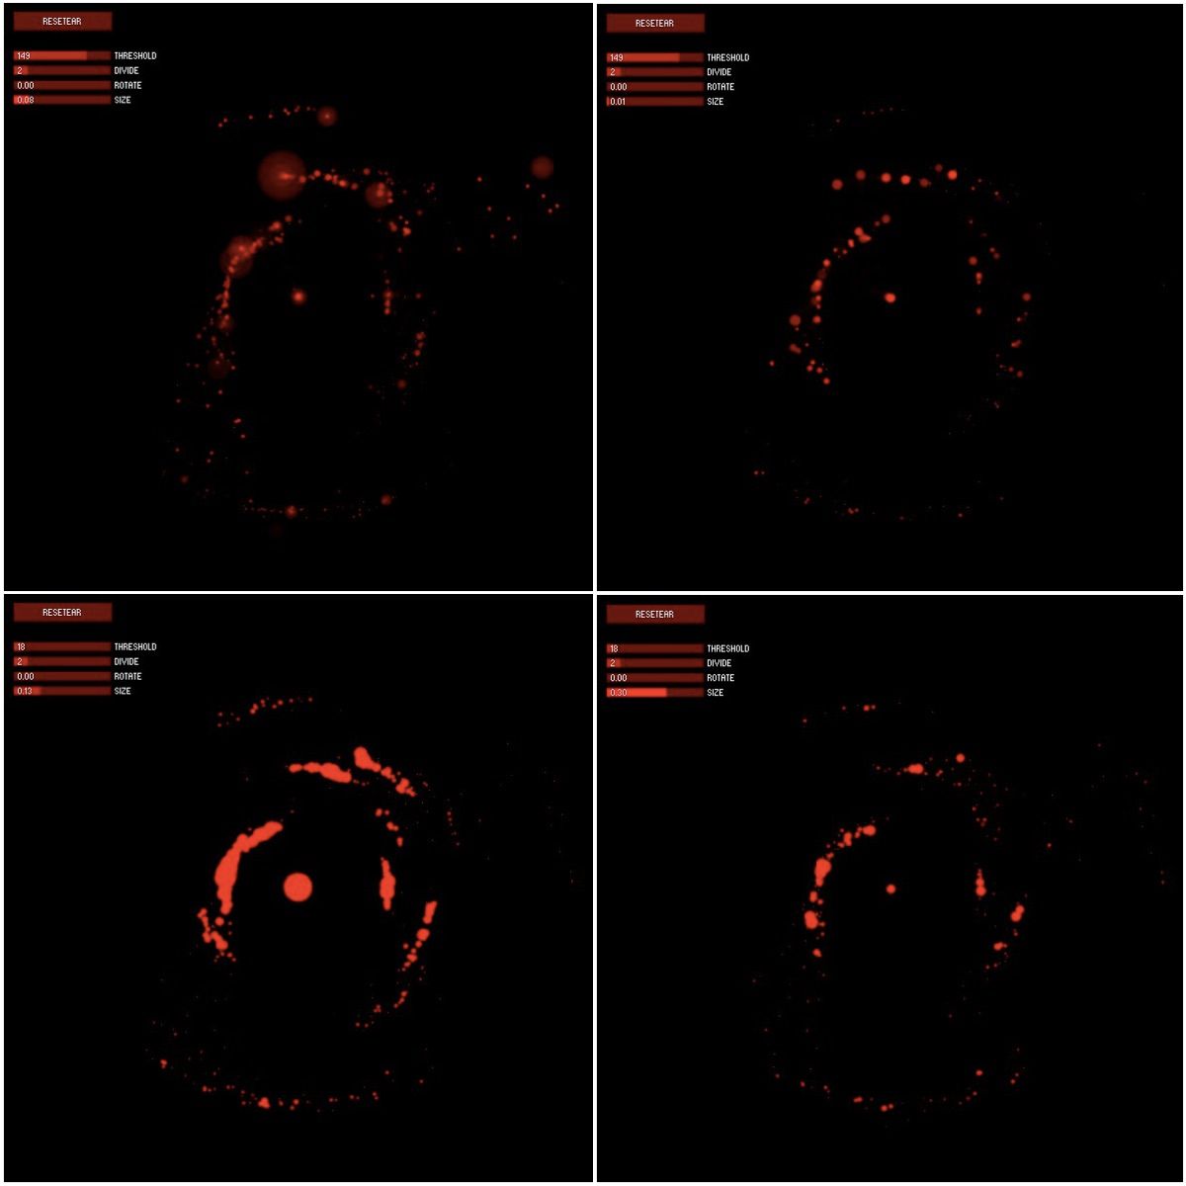
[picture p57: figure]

Cada “banda” que se forma, representa un árbol. En la imagen se muestran varias configuraciones de formación de cluster.

## Extensiones Necesarias

- Con los puntos agrupados, es necesario extender el análisis para determinar los diámetros. Este trabajo requiere un ensayo experimental tanto en campo, como en medidas diamétricas exactas para calibrara el algoritmo. Con medidas diamétricas exactas, nos referimos a estructuras cilíndricas de diámetro exacto que son escaneadas por el escáner LIDAR, para determinar los diámetros y validar el algoritmo de reconocimiento de troncos, así como extenderlo para la medición de diámetros y cálculo de área basal y de diámetros.
- La forma de exportar datos todavía no es directa, para ellos hay que grabar los datos en la consola terminal y exportar a archivo separado por comas

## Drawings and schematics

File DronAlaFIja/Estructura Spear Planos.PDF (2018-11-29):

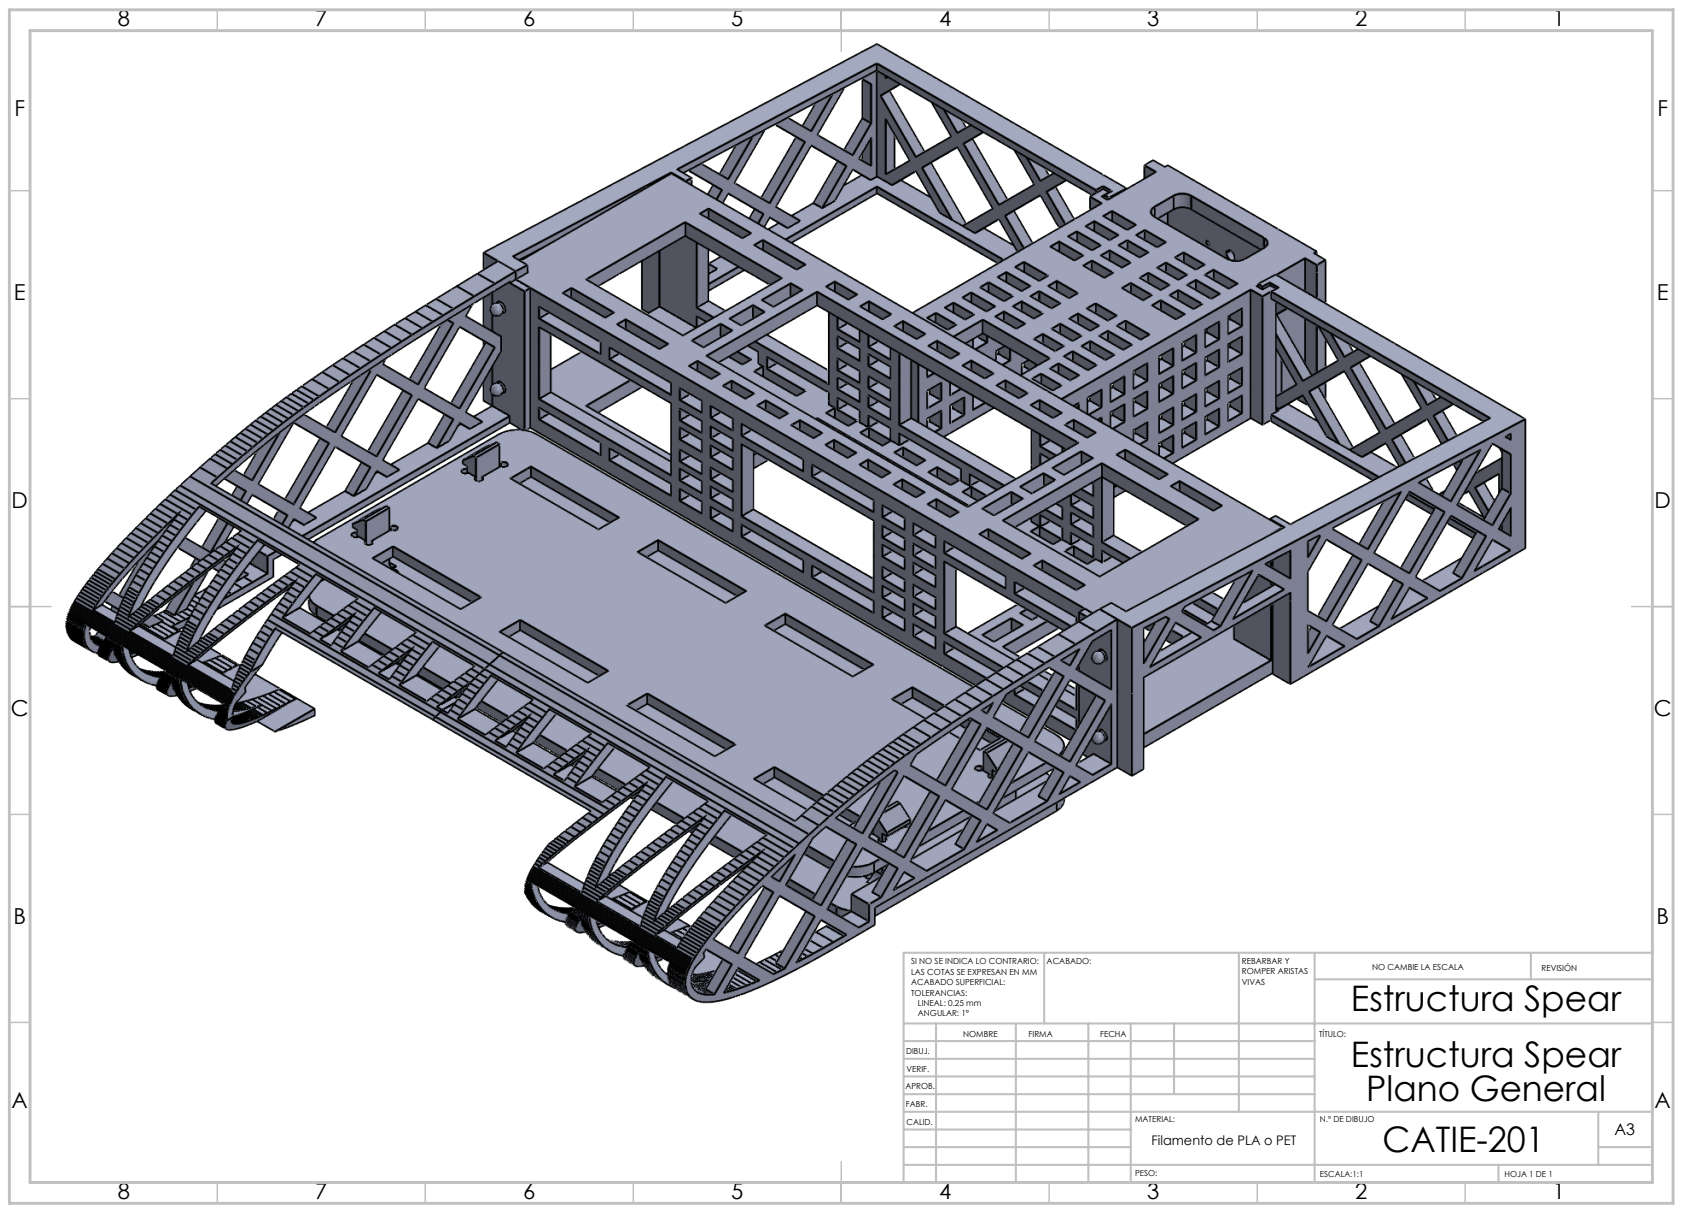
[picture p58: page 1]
ACABADO:; REBARBAR Y; ROMPER ARISTAS; NO CAMBIE LA ESCALA; REVISIÓN; ESCALA:1:1; HOJA 1 DE 1; Estructura Spear

SI NO SE INDICA LO CONTRARIO:
LAS COTAS SE EXPRESAN EN MM
ACABADO SUPERFICIAL:
TOLERANCIAS:
LINEAL: 0.25 mm
ANGULAR: 1°

NOMBRE | FIRMA | FECHA | | | | TÍTULO: Estructura Spear Plano General

DIBUJ.
VERIF.
APROB.
FABR.
CALID. | | | | MATERIAL: | N.º DE DIBUJO CATIE-201 | A3 Filamento de PLA o PET

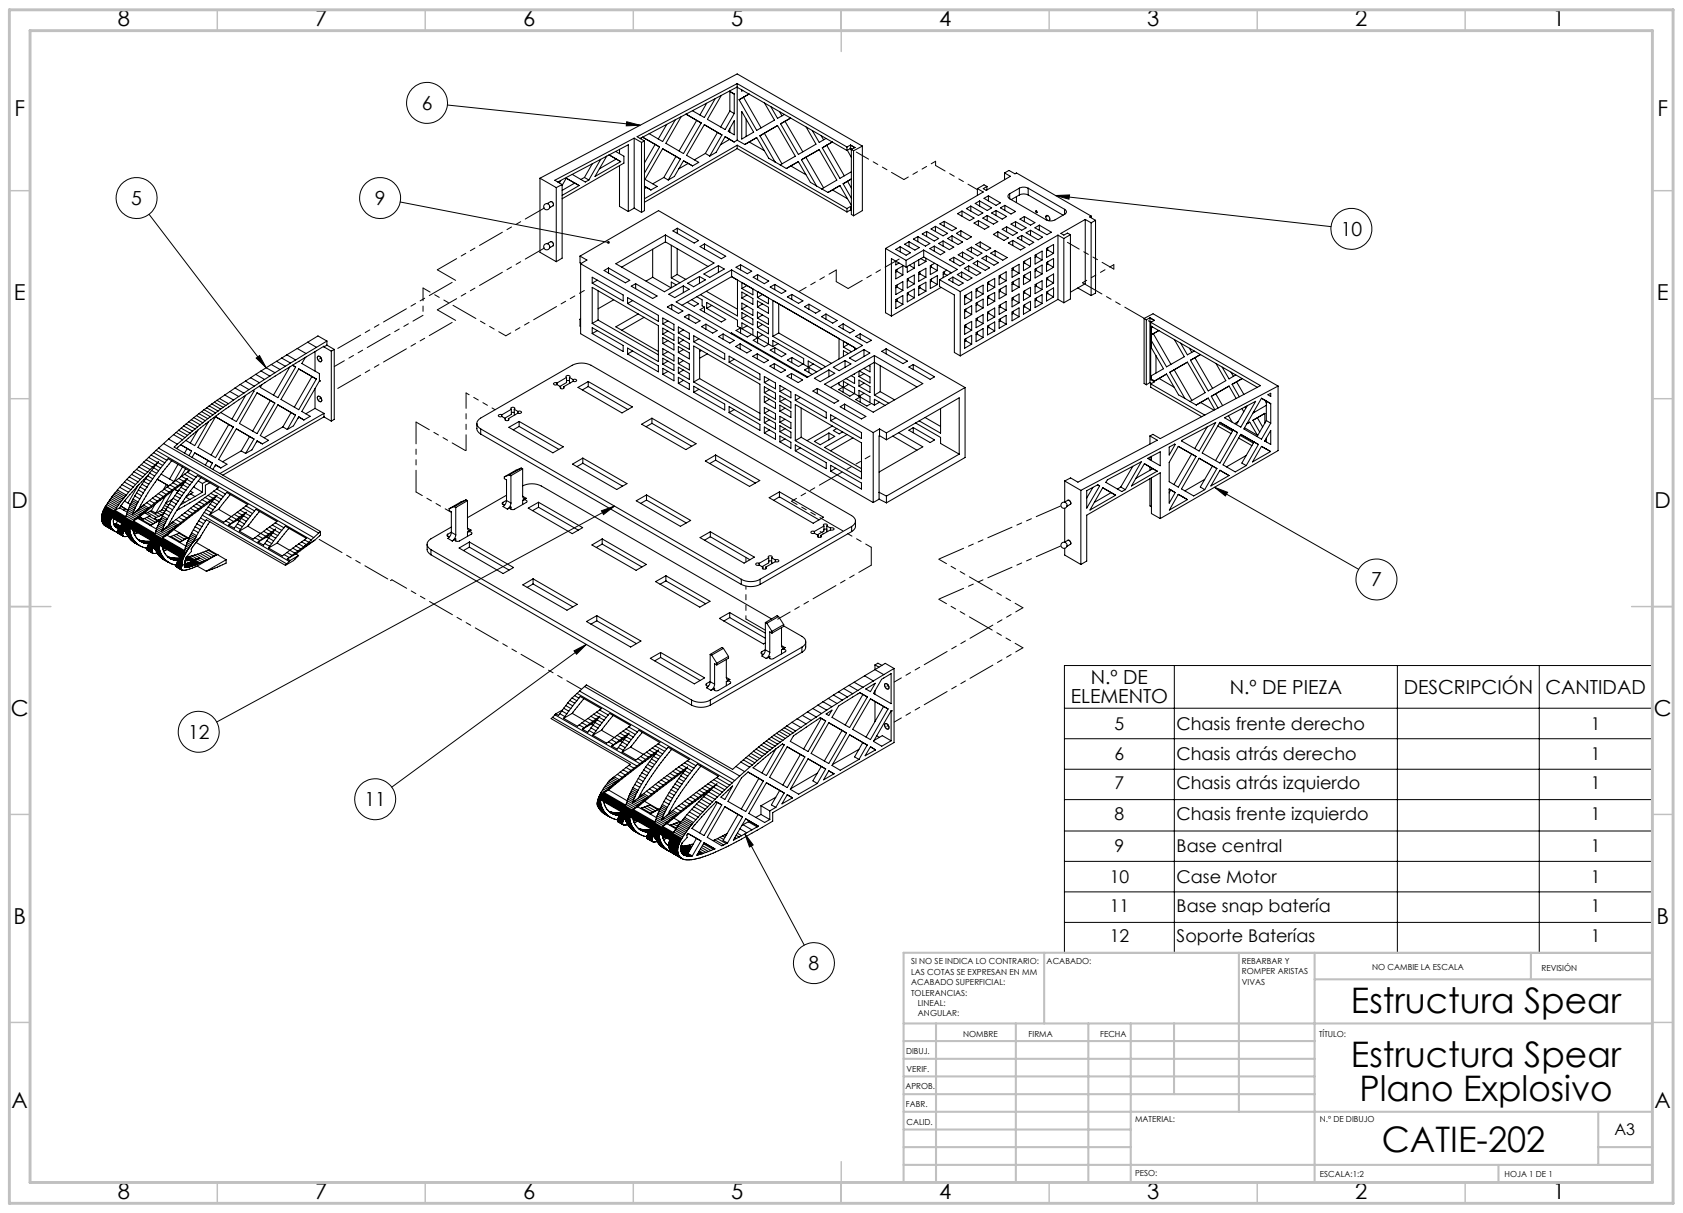
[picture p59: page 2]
ESCALA:1:2; HOJA 1 DE 1; Estructura Spear

N.º DE ELEMENTO | N.º DE PIEZA | DESCRIPCIÓN | CANTIDAD

5 | Chasis frente derecho | | 1
6 | Chasis atrás derecho | | 1
7 | Chasis atrás izquierdo | | 1
8 | Chasis frente izquierdo | | 1
9 | Base central | | 1
10 | Case Motor | | 1
11 | Base snap batería | | 1
12 | Soporte Baterías | | 1

SI NO SE INDICA LO CONTRARIO: LAS COTAS SE EXPRESAN EN MM ACABADO SUPERFICIAL: TOLERANCIAS: LINEAL: ANGULAR: | ACABADO: | REBARBAR Y ROMPER ARISTAS VIVAS | NO CAMBIE LA ESCALA | REVISIÓN

NOMBRE | FIRMA | FECHA | | | TÍTULO: Estructura Spear Plano Explosivo

DIBUJ.
VERIF.
APROB.
FABR.

MATERIAL: | A3

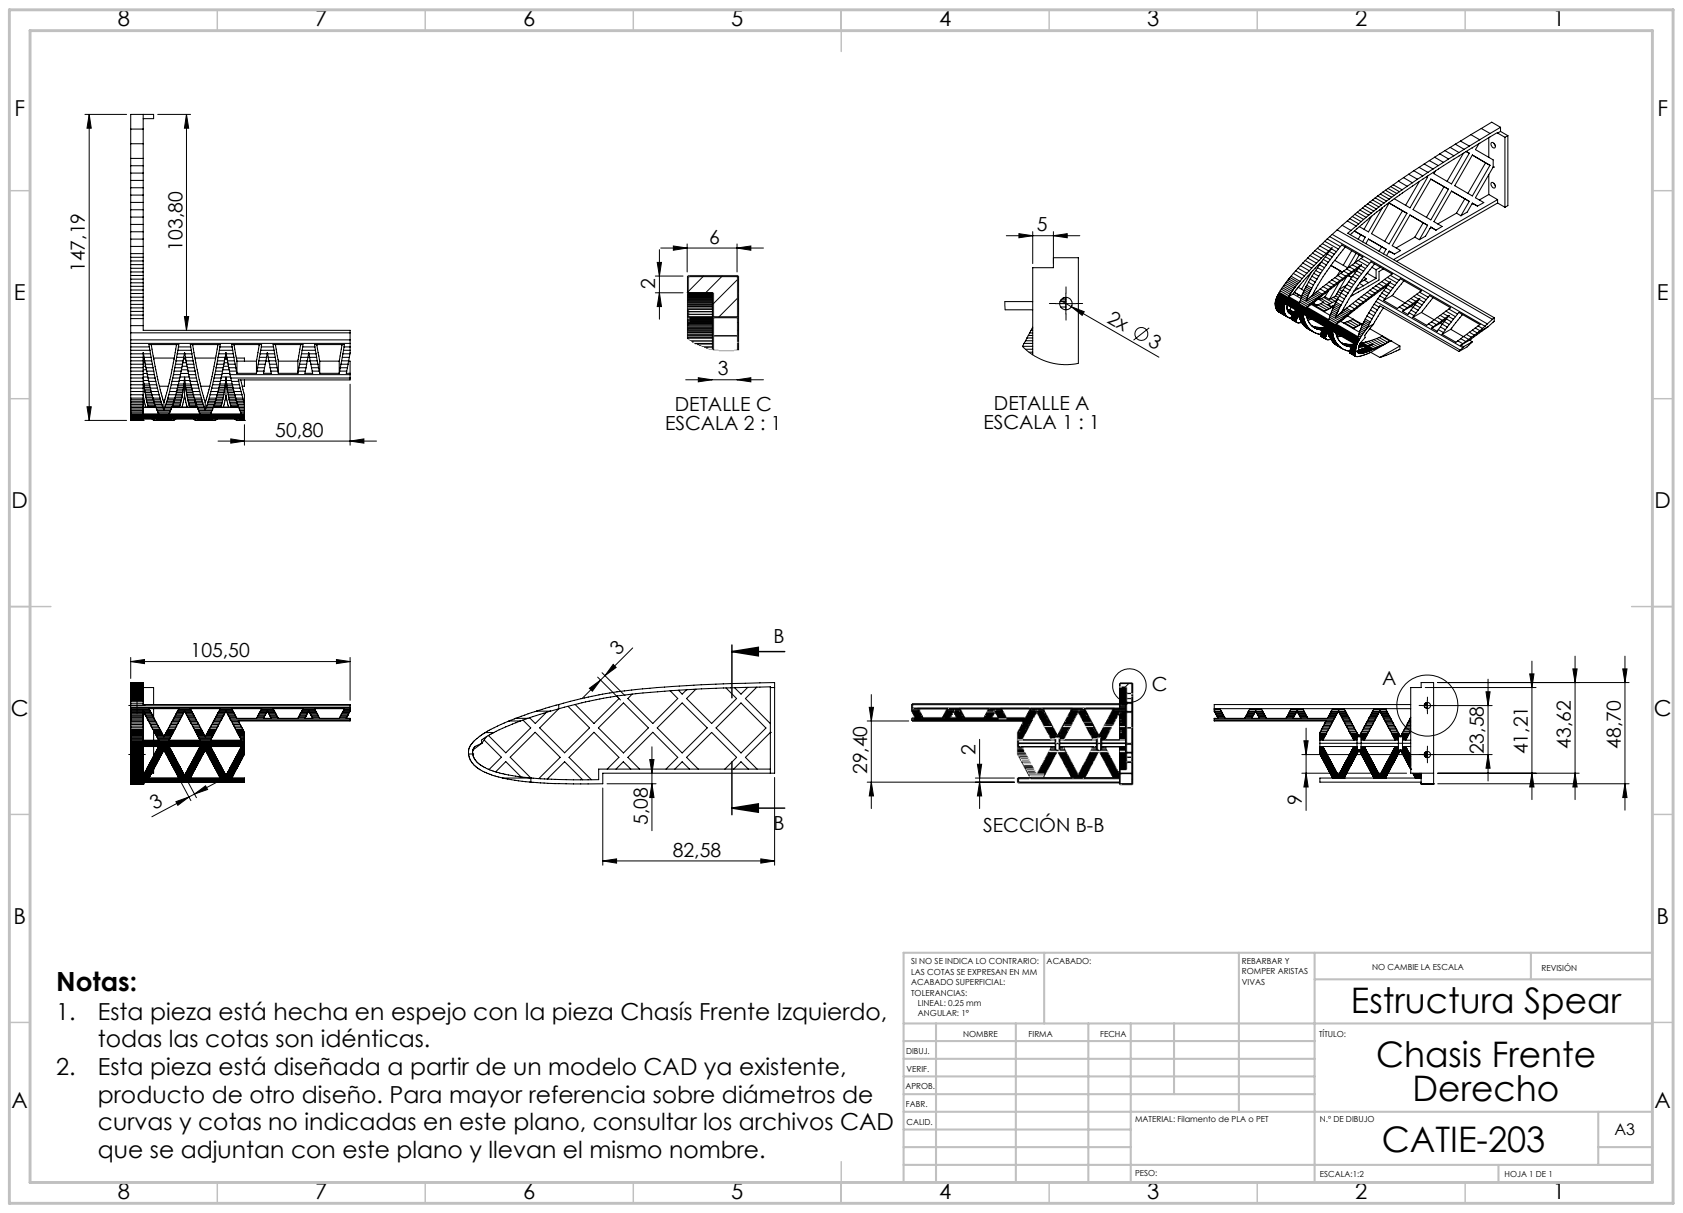
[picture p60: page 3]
DETALLE A ESCALA 1 : 1; SECCIÓN B-B; DETALLE C ESCALA 2 : 1; ACABADO:; REBARBAR Y; ROMPER ARISTAS; NO CAMBIE LA ESCALA; REVISIÓN; Estructura Spear

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

Notas:
1. Esta pieza está hecha en espejo con la pieza Chasís Frente Izquierdo,
todas las cotas son idénticas.
2. Esta pieza está diseñada a partir de un modelo CAD ya existente,
producto de otro diseño. Para mayor referencia sobre diámetros de
curvas y cotas no indicadas en este plano, consultar los archivos CAD
que se adjuntan con este plano y llevan el mismo nombre.

NOMBRE | FIRMA | FECHA | | TÍTULO: Chasis Frente Derecho

DIBUJ.
VERIF.
APROB.
FABR.

MATERIAL: Filamento de PLA o PET

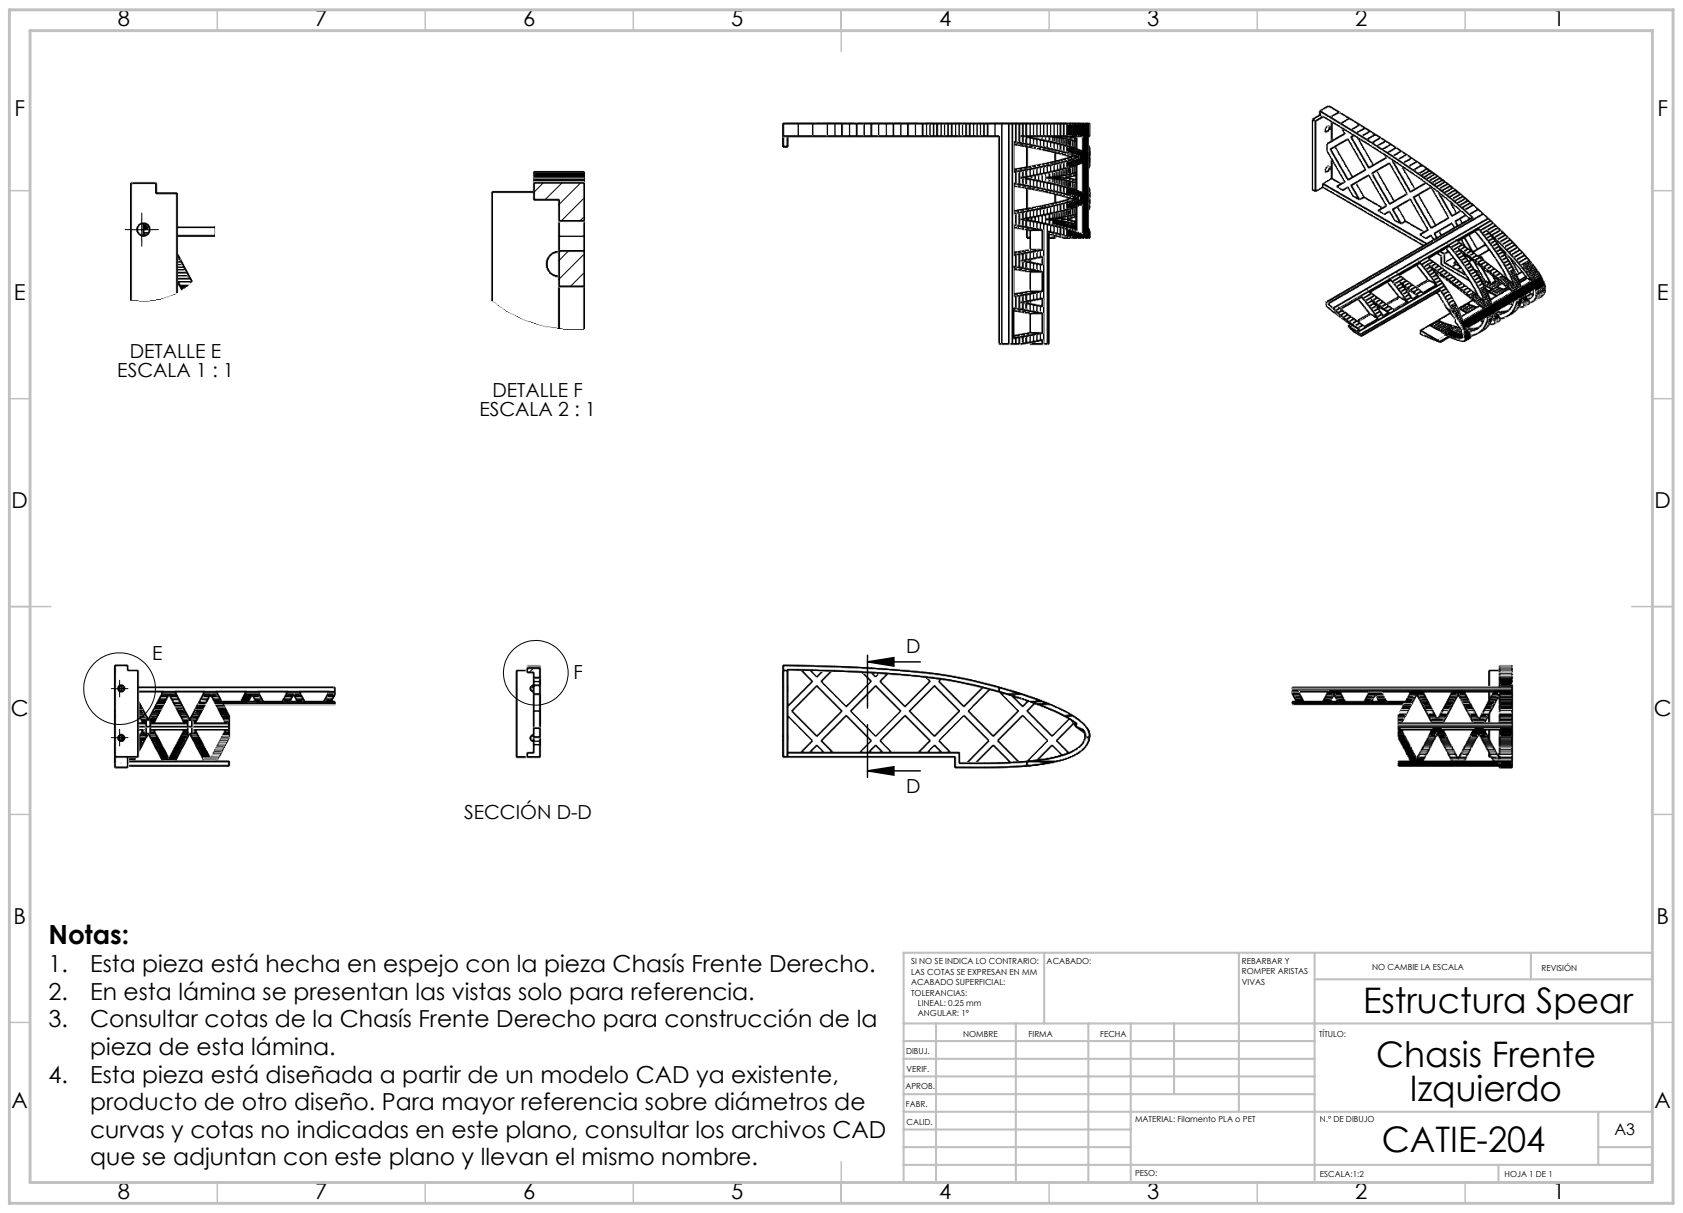
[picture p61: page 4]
SECCIÓN D-D; DETALLE E ESCALA 1 : 1; DETALLE F ESCALA 2 : 1; ACABADO:; REBARBAR Y; ROMPER ARISTAS; NO CAMBIE LA ESCALA; REVISIÓN; Estructura Spear

Notas:
1. Esta pieza está hecha en espejo con la pieza Chasís Frente Derecho.
2. En esta lámina se presentan las vistas solo para referencia.
3. Consultar cotas de la Chasís Frente Derecho para construcción de la
pieza de esta lámina.
4. Esta pieza está diseñada a partir de un modelo CAD ya existente,
producto de otro diseño. Para mayor referencia sobre diámetros de
curvas y cotas no indicadas en este plano, consultar los archivos CAD

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

NOMBRE | FIRMA | FECHA | | TÍTULO: Chasis Frente Izquierdo

DIBUJ.
VERIF.
APROB.
FABR.

MATERIAL: Filamento PLA o PET

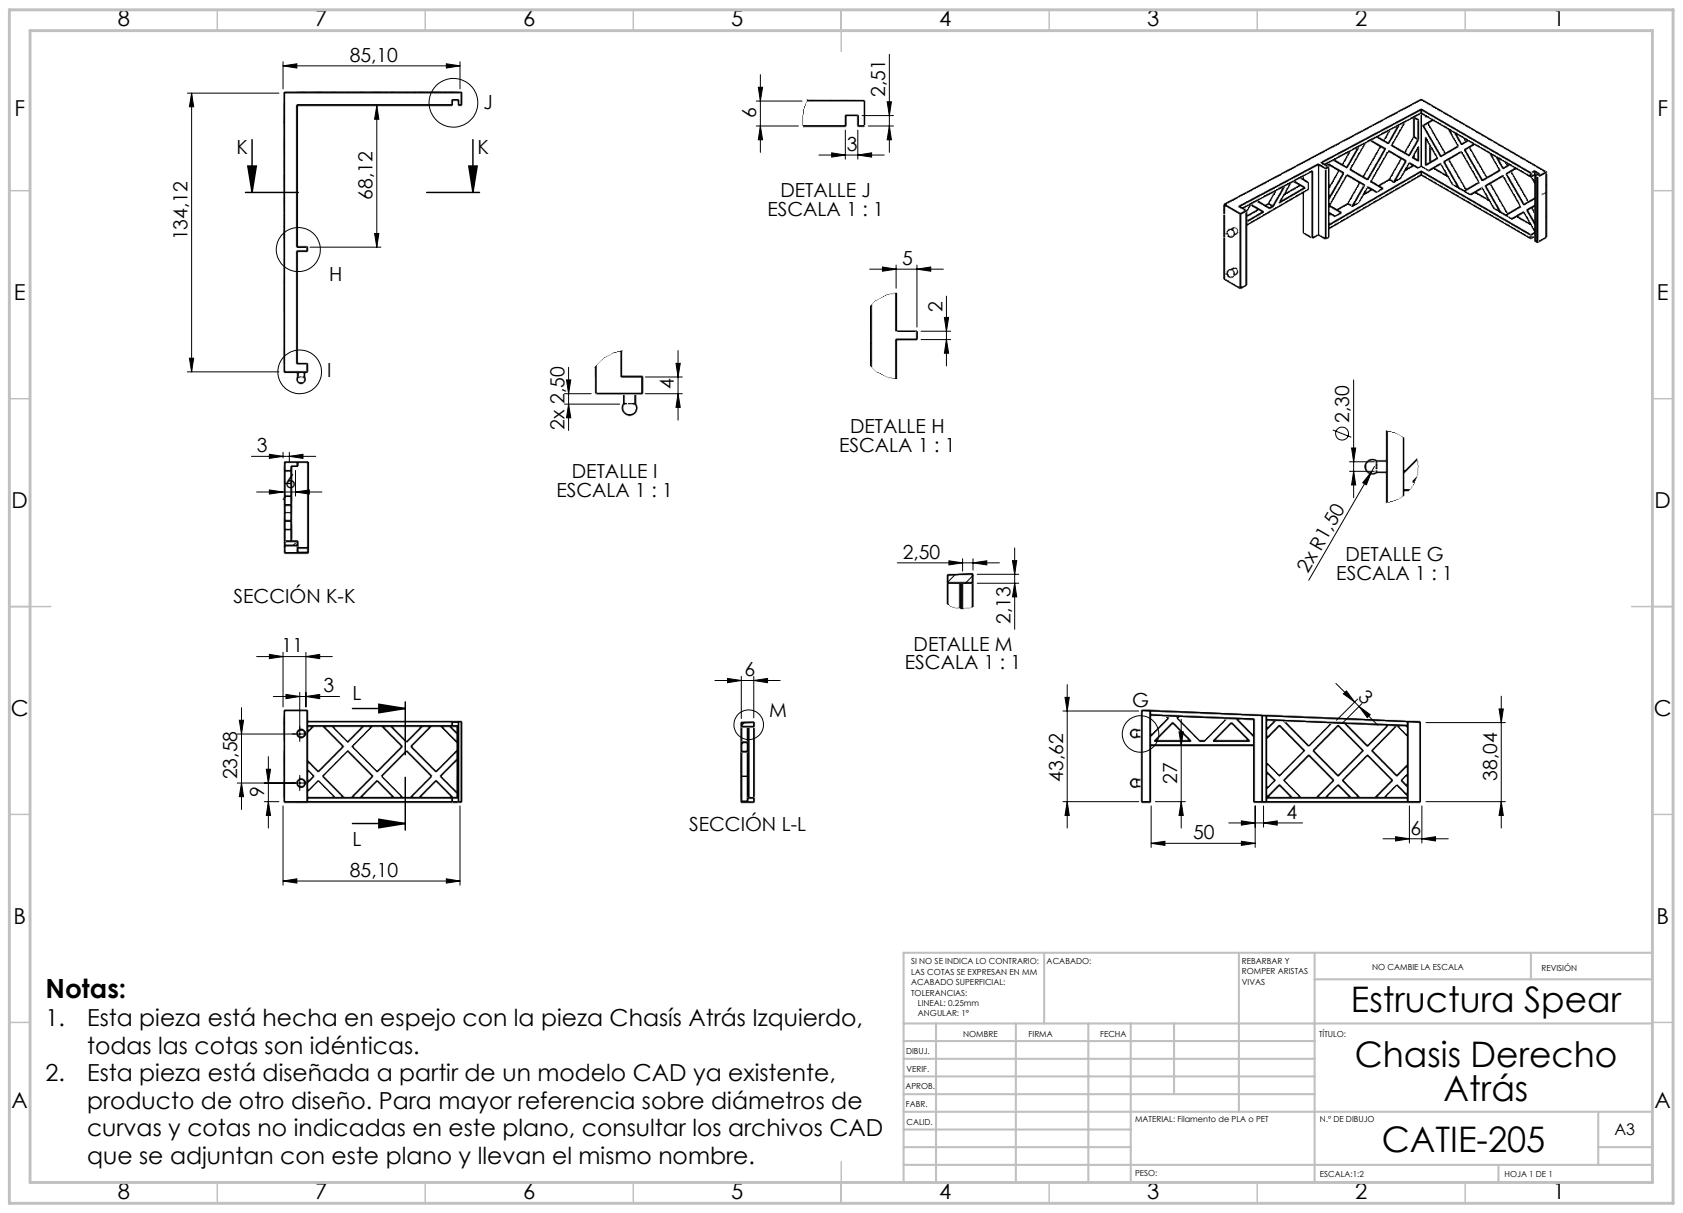
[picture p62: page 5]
DETALLE G ESCALA 1 : 1; DETALLE H ESCALA 1 : 1; DETALLE I ESCALA 1 : 1; DETALLE J ESCALA 1 : 1; SECCIÓN K-K; SECCIÓN L-L; DETALLE M ESCALA 1 : 1; ACABADO:; REBARBAR Y; ROMPER ARISTAS; NO CAMBIE LA ESCALA; REVISIÓN; Estructura Spear

SI NO SE INDICA LO CONTRARIO:
LAS COTAS SE EXPRESAN EN MM
ACABADO SUPERFICIAL:
TOLERANCIAS:
LINEAL: 0.25mm
ANGULAR: 1°

Notas:
1. Esta pieza está hecha en espejo con la pieza Chasís Atrás Izquierdo,
todas las cotas son idénticas.
2. Esta pieza está diseñada a partir de un modelo CAD ya existente,
producto de otro diseño. Para mayor referencia sobre diámetros de
curvas y cotas no indicadas en este plano, consultar los archivos CAD

NOMBRE | FIRMA | FECHA | TÍTULO: Chasis Derecho Atrás

DIBUJ.
VERIF.
APROB.
FABR.

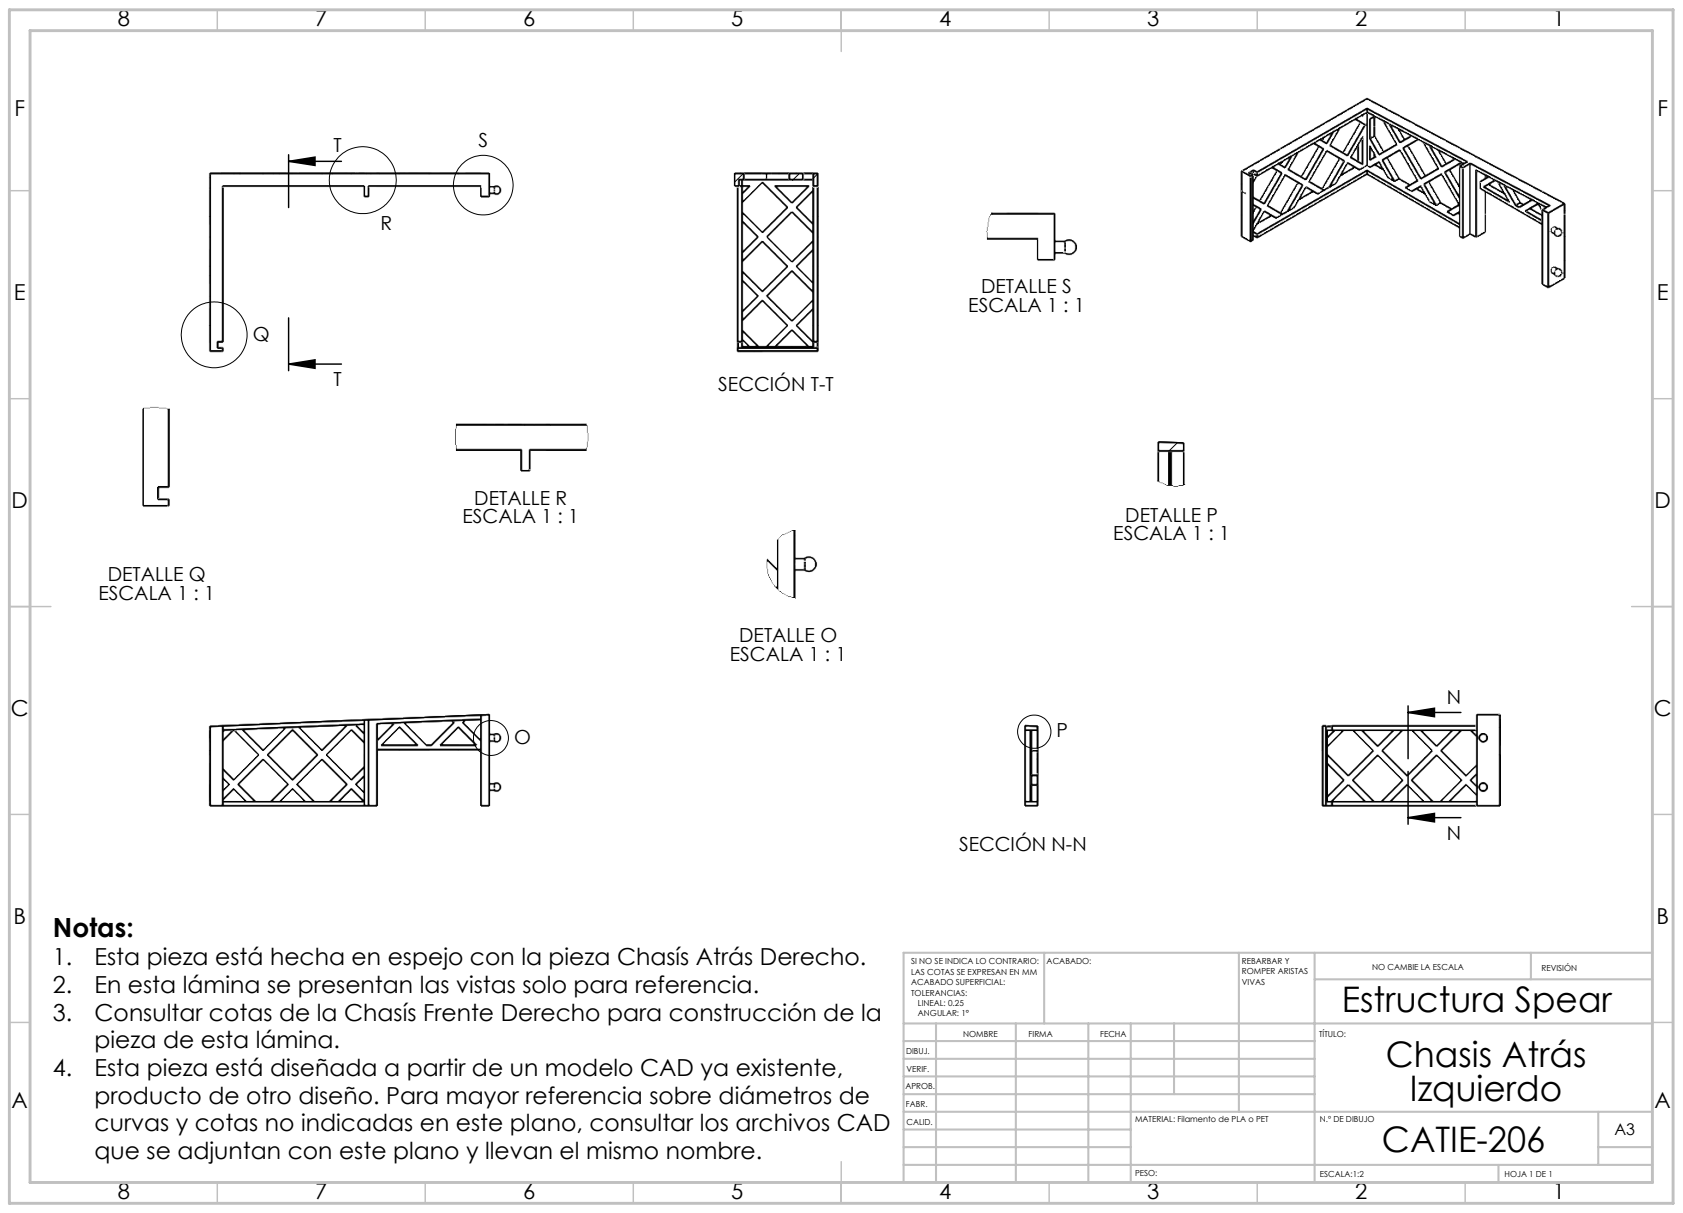
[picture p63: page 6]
SECCIÓN N-N; DETALLE O ESCALA 1 : 1; DETALLE P ESCALA 1 : 1; DETALLE Q ESCALA 1 : 1; DETALLE R ESCALA 1 : 1; DETALLE S ESCALA 1 : 1; SECCIÓN T-T; ACABADO:; REBARBAR Y; ROMPER ARISTAS; NO CAMBIE LA ESCALA; REVISIÓN; Estructura Spear

Notas:
1. Esta pieza está hecha en espejo con la pieza Chasís Atrás Derecho.
2. En esta lámina se presentan las vistas solo para referencia.
3. Consultar cotas de la Chasís Frente Derecho para construcción de la
pieza de esta lámina.
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

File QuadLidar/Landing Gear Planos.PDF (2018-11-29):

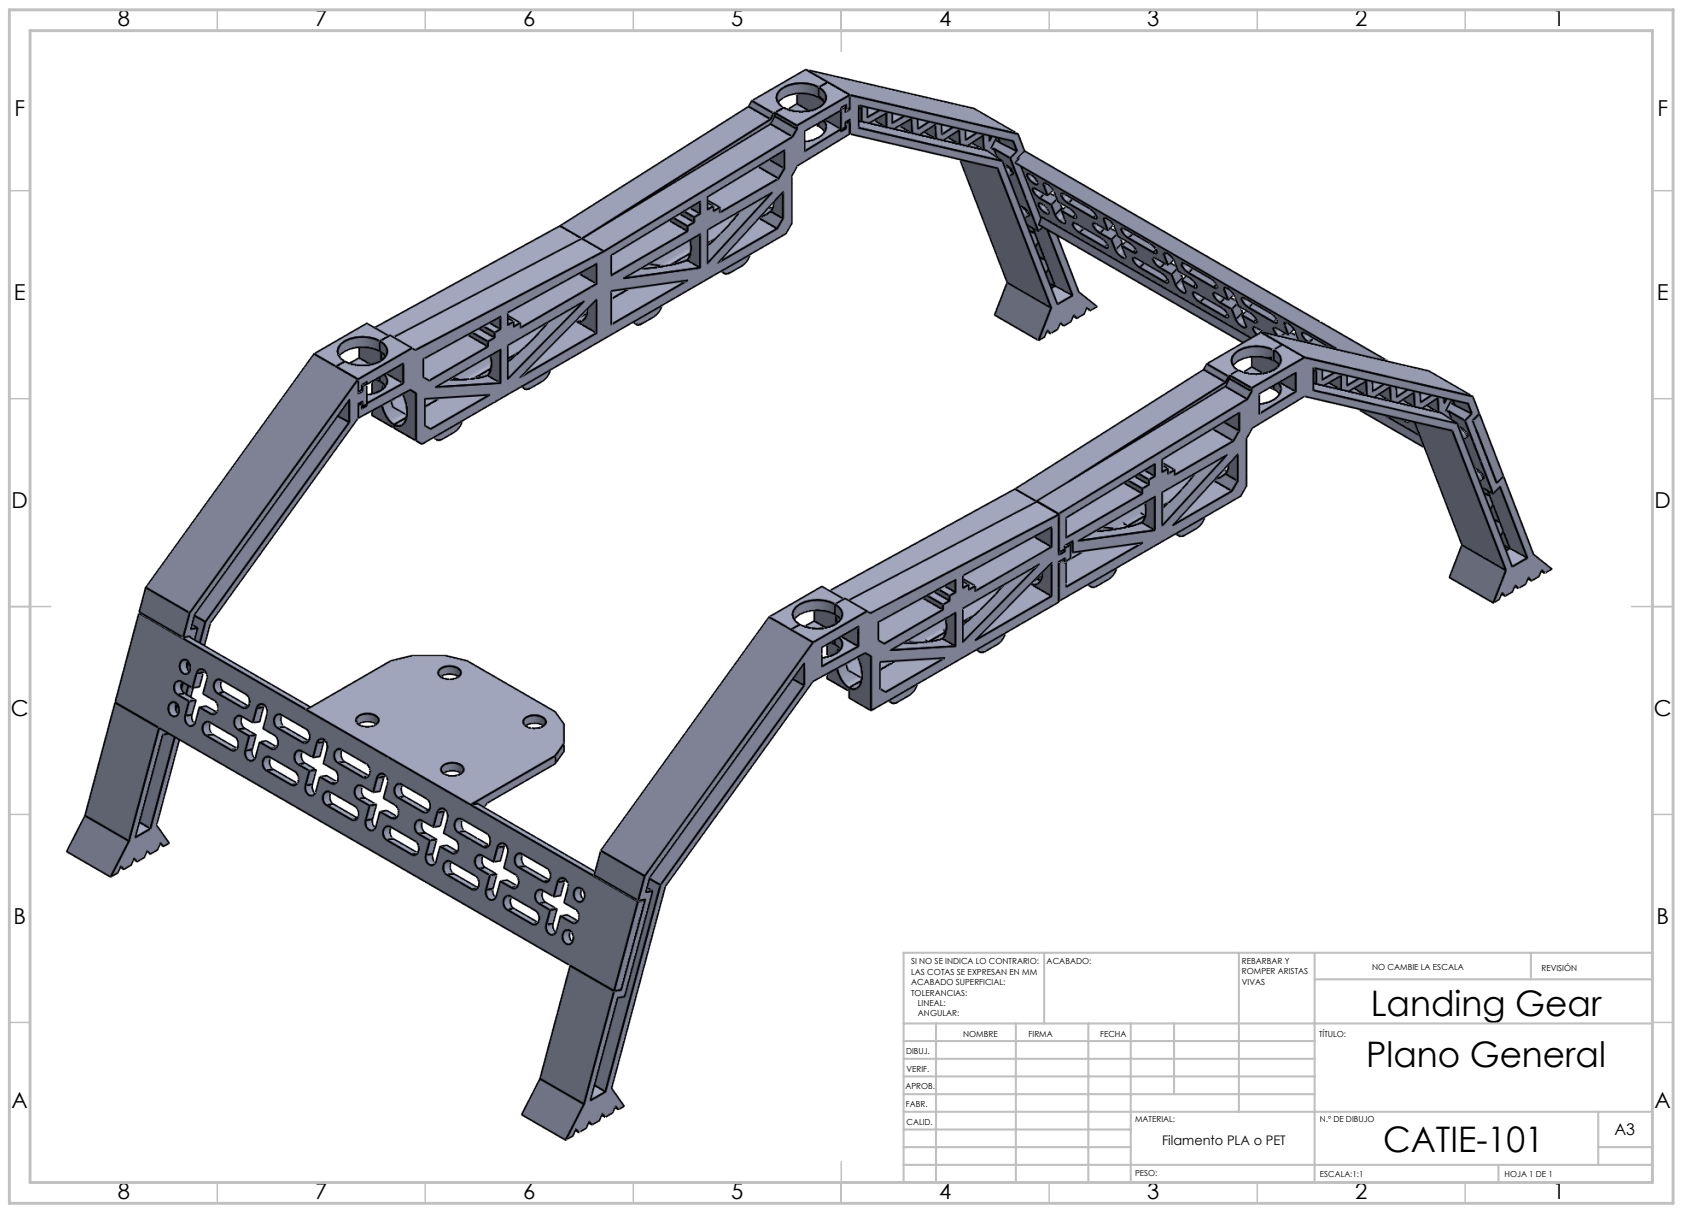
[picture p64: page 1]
ACABADO:; REBARBAR Y; ROMPER ARISTAS; NO CAMBIE LA ESCALA; REVISIÓN; ESCALA:1:1; HOJA 1 DE 1; Landing Gear

SI NO SE INDICA LO CONTRARIO:
LAS COTAS SE EXPRESAN EN MM
ACABADO SUPERFICIAL:
TOLERANCIAS:
LINEAL:
ANGULAR:

NOMBRE | FIRMA | FECHA | | | | TÍTULO: Plano General

DIBUJ.
VERIF.
APROB.
FABR.
CALID. | | | | MATERIAL: | N.º DE DIBUJO CATIE-101 | A3 Filamento PLA o PET

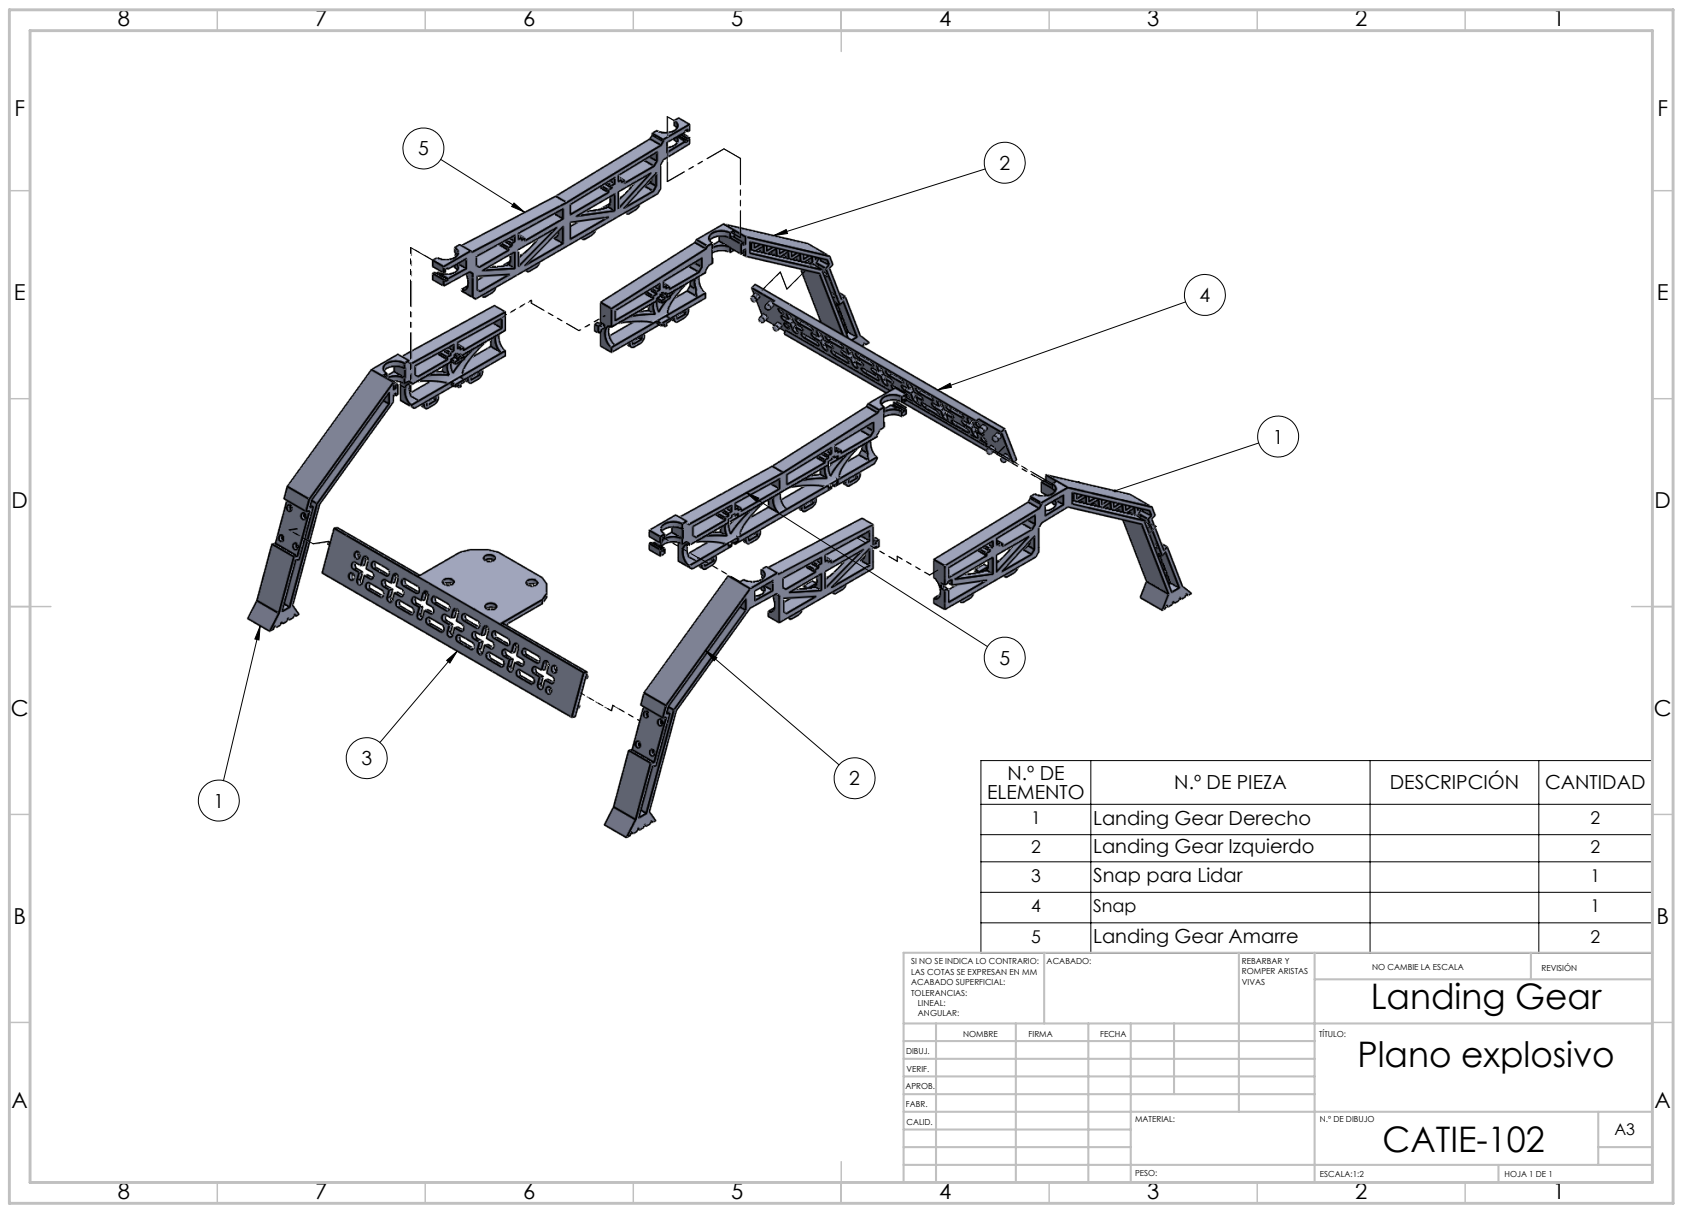
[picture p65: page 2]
ESCALA:1:2; HOJA 1 DE 1; Landing Gear

N.º DE ELEMENTO | N.º DE PIEZA | DESCRIPCIÓN | CANTIDAD
1 | Landing Gear Derecho | | 2
2 | Landing Gear Izquierdo | | 2
3 | Snap para Lidar | | 1
4 | Snap | | 1
5 | Landing Gear Amarre | | 2

SI NO SE INDICA LO CONTRARIO: LAS COTAS SE EXPRESAN EN MM ACABADO SUPERFICIAL: TOLERANCIAS: LINEAL: ANGULAR: | ACABADO: | REBARBAR Y ROMPER ARISTAS VIVAS | NO CAMBIE LA ESCALA | REVISIÓN

NOMBRE | FIRMA | FECHA | | | TÍTULO: Plano explosivo

DIBUJ.
VERIF.
APROB.
FABR.

MATERIAL: | A3

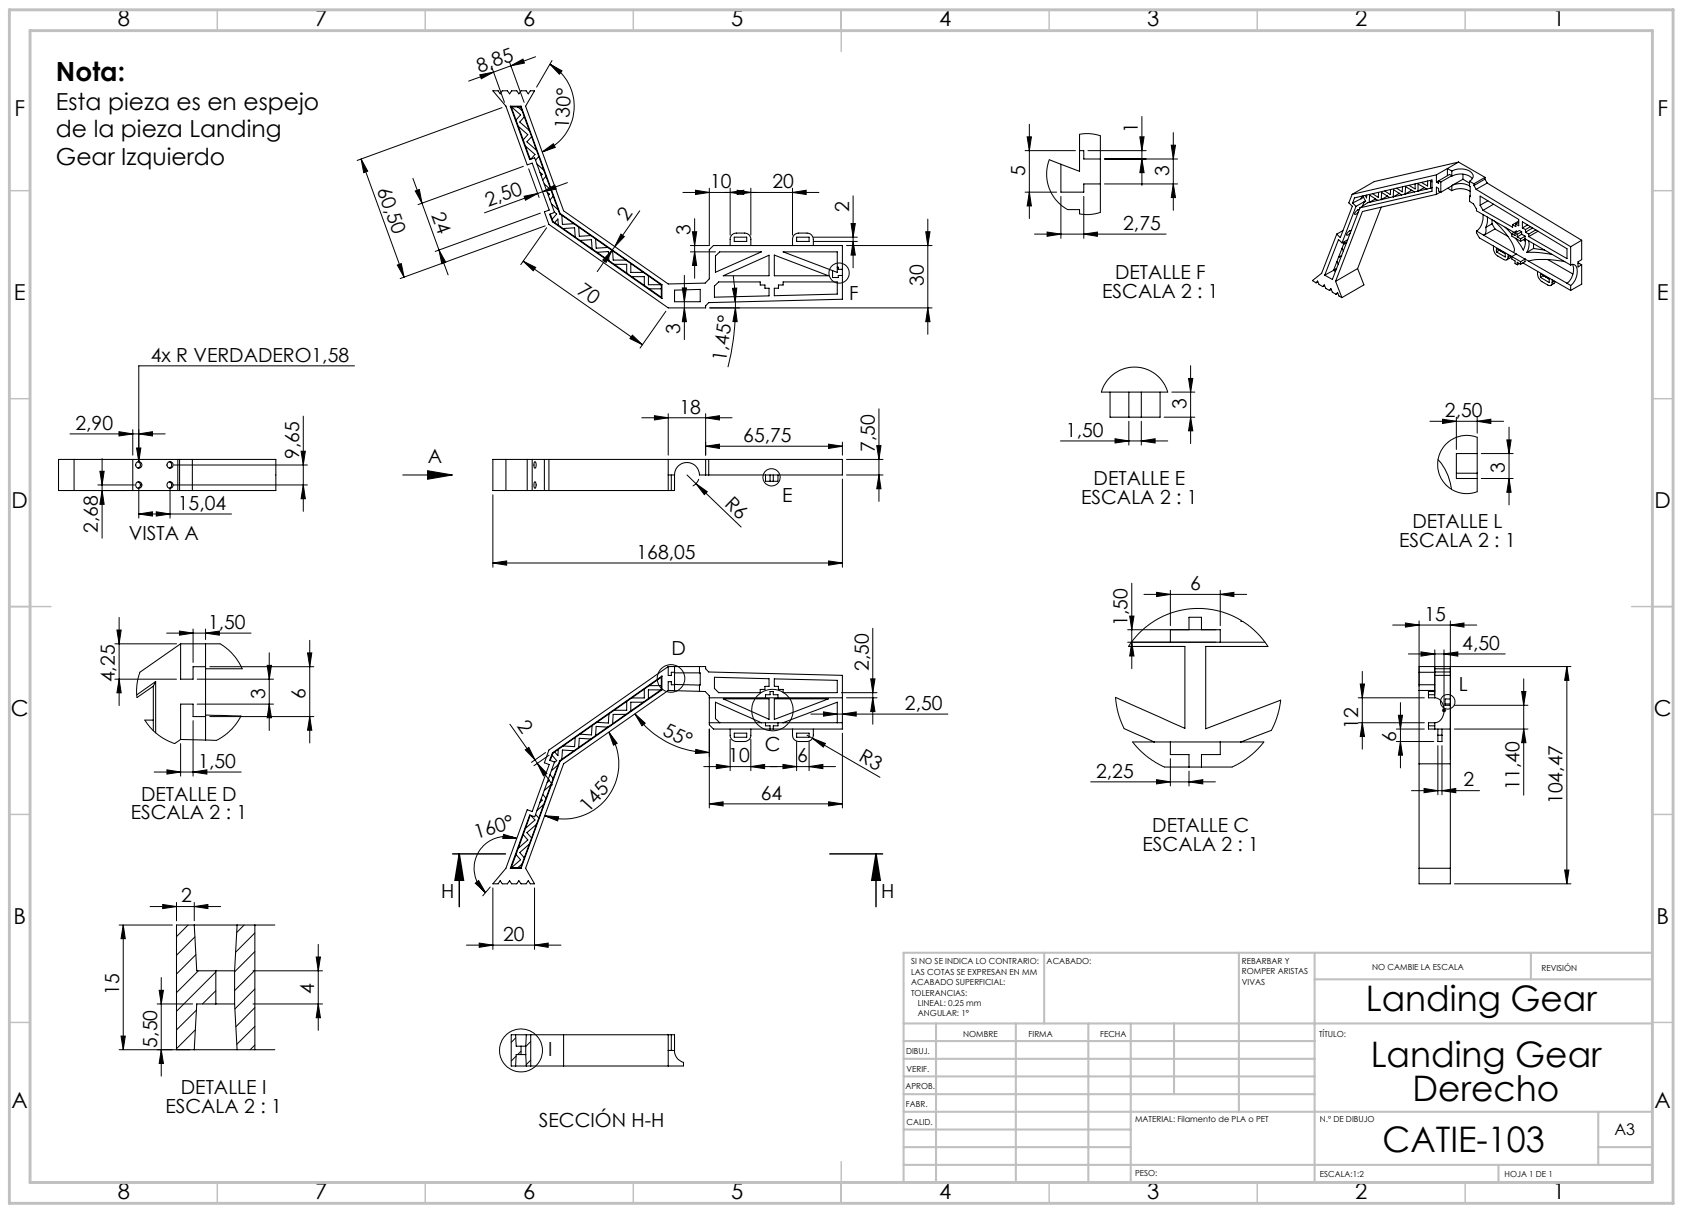
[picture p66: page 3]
4x R VERDADERO1,58; VISTA A; DETALLE C ESCALA 2 : 1; DETALLE D ESCALA 2 : 1; DETALLE E ESCALA 2 : 1; DETALLE F ESCALA 2 : 1; SECCIÓN H-H; DETALLE I ESCALA 2 : 1; DETALLE L ESCALA 2 : 1; ACABADO:; REBARBAR Y; ROMPER ARISTAS; NO CAMBIE LA ESCALA; REVISIÓN; Landing Gear

Nota:
Esta pieza es en espejo
de la pieza Landing
Gear Izquierdo

SI NO SE INDICA LO CONTRARIO:
LAS COTAS SE EXPRESAN EN MM
ACABADO SUPERFICIAL:
TOLERANCIAS:
LINEAL: 0.25 mm
ANGULAR: 1°

NOMBRE | FIRMA | FECHA | | TÍTULO: Landing Gear Derecho

DIBUJ.
VERIF.
APROB.
FABR.

MATERIAL: Filamento de PLA o PET

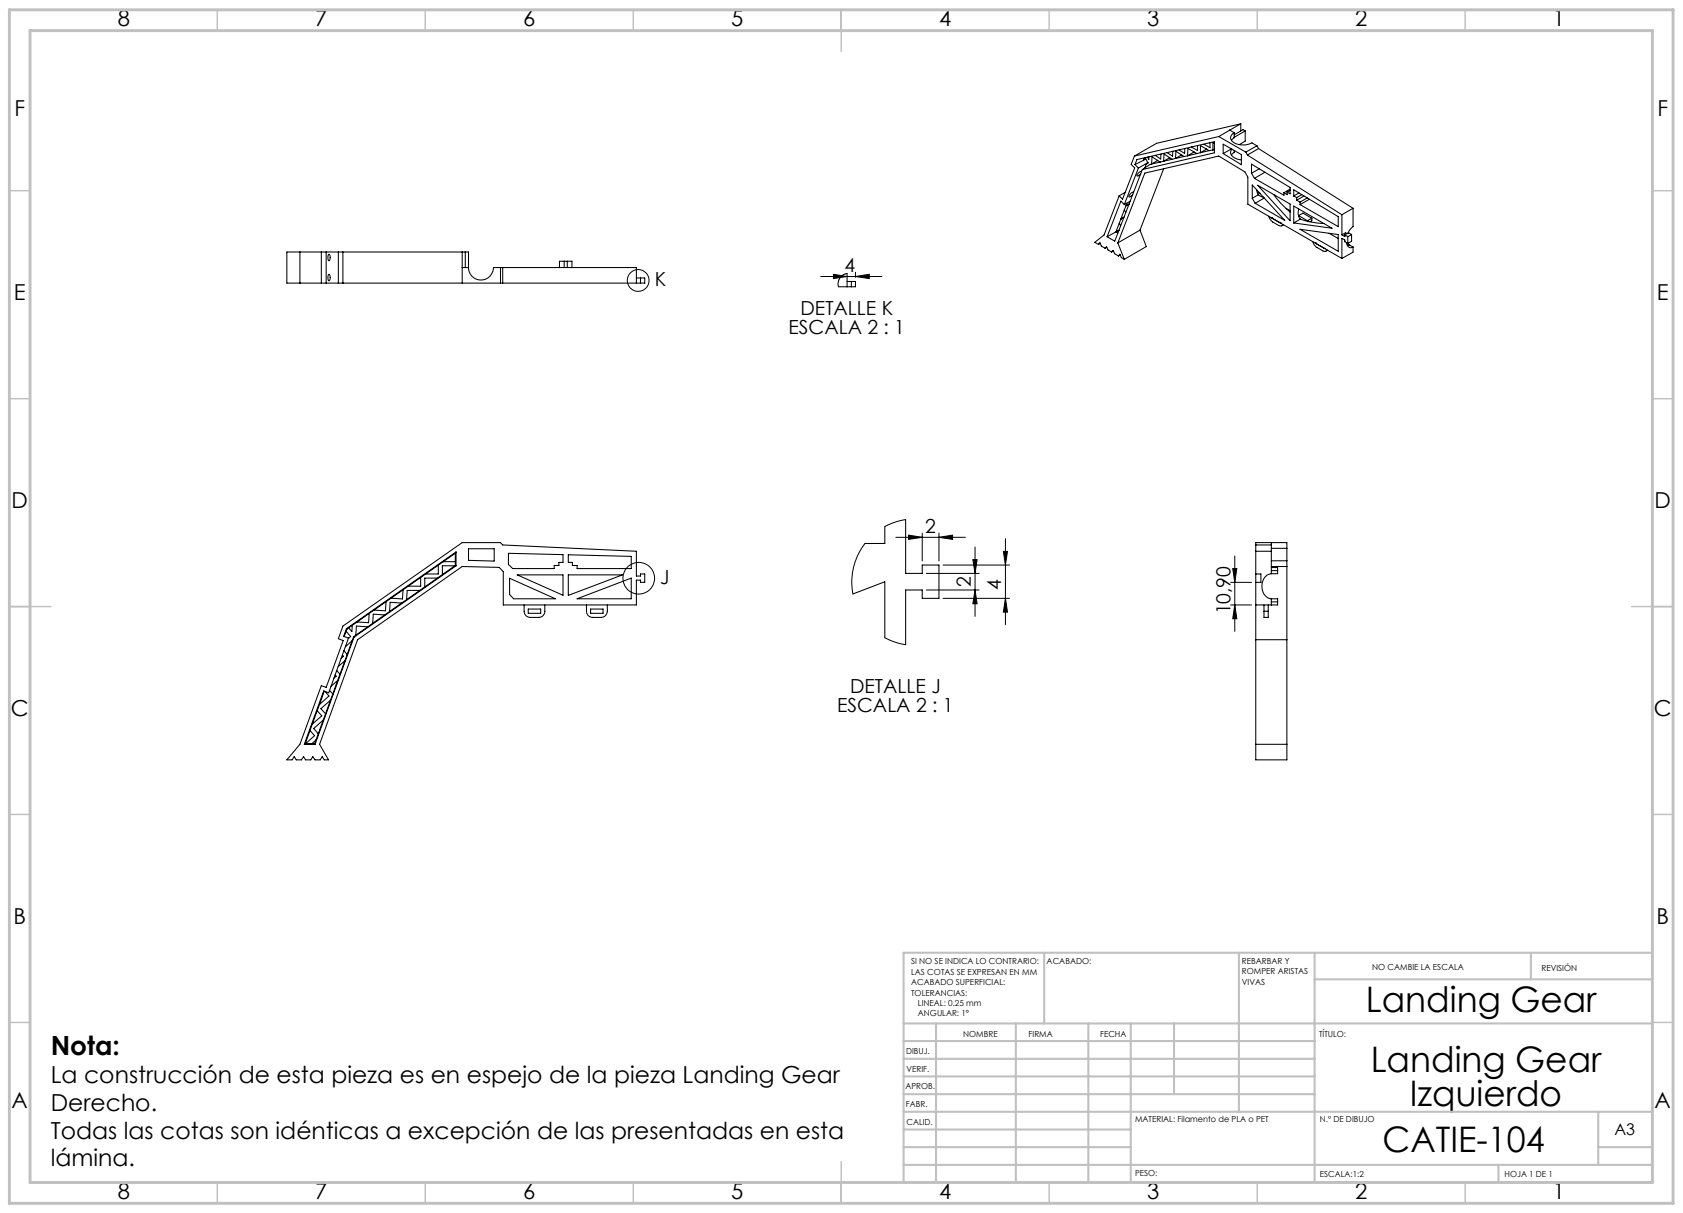
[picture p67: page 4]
DETALLE J ESCALA 2 : 1; DETALLE K ESCALA 2 : 1; ACABADO:; REBARBAR Y; ROMPER ARISTAS; NO CAMBIE LA ESCALA; REVISIÓN; Landing Gear

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

Nota:
La construcción de esta pieza es en espejo de la pieza Landing Gear
Derecho.
Todas las cotas son idénticas a excepción de las presentadas en esta
lámina.

NOMBRE | FIRMA | FECHA | TÍTULO: Landing Gear

DIBUJ.
VERIF.
APROB.
FABR.

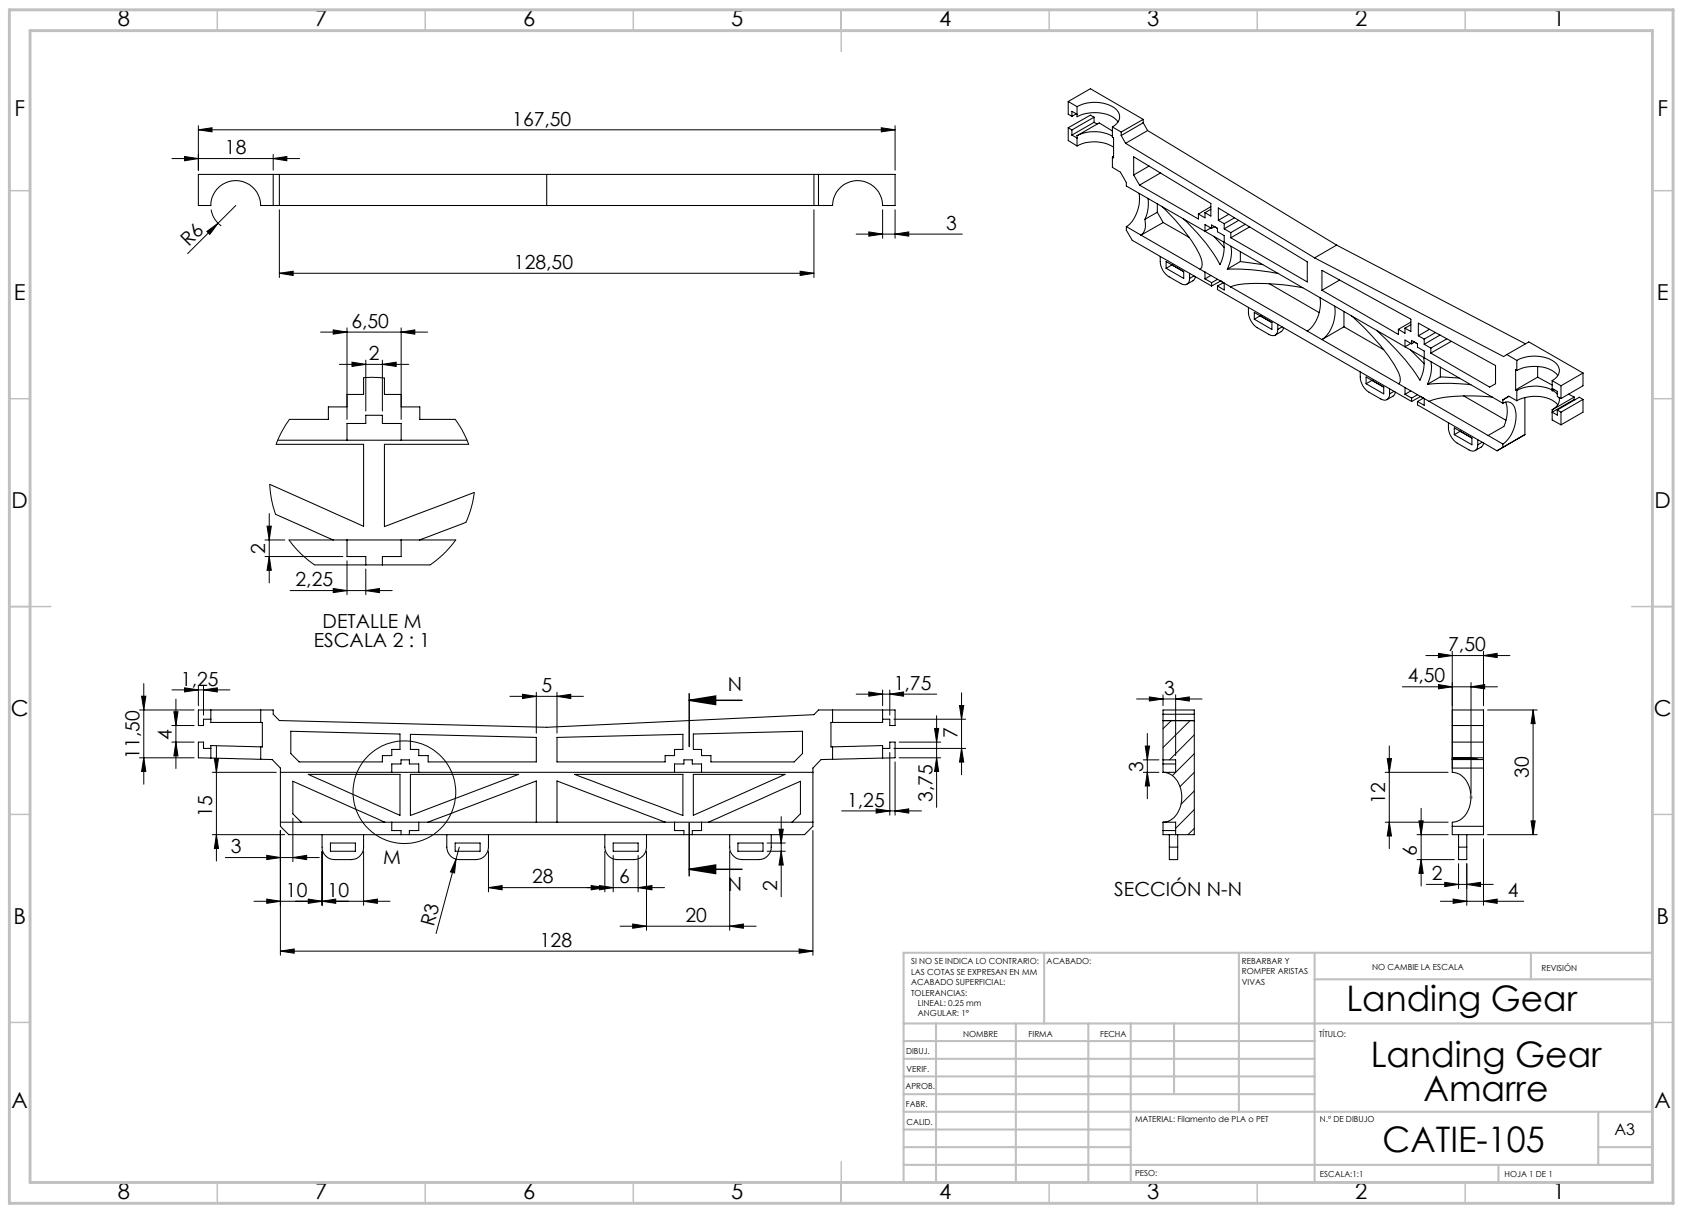
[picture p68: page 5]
DETALLE M ESCALA 2 : 1; SECCIÓN N-N; ACABADO:; REBARBAR Y; ROMPER ARISTAS; NO CAMBIE LA ESCALA; REVISIÓN; Landing Gear

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

NOMBRE | FIRMA | FECHA | TÍTULO: Landing Gear Amarre

DIBUJ.
VERIF.
APROB.
FABR.

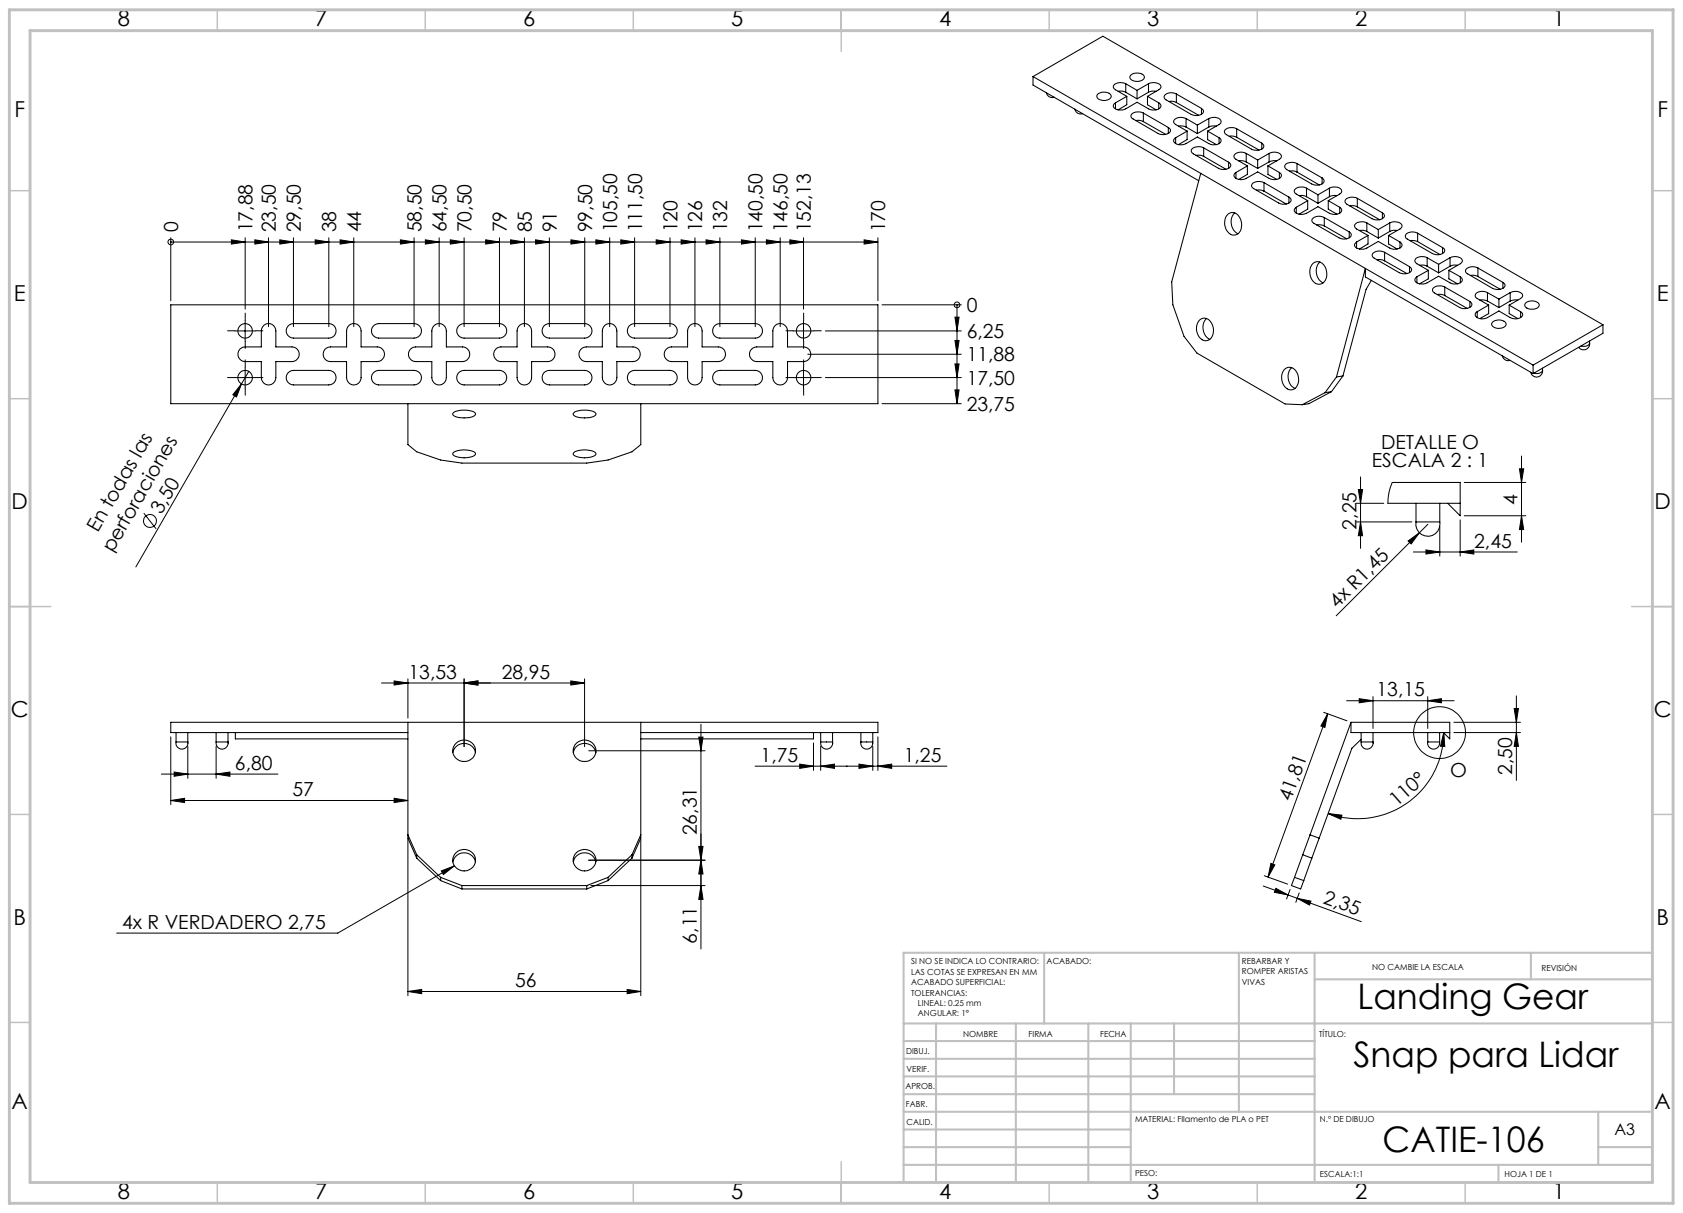
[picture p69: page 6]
4x R VERDADERO 2,75; DETALLE O ESCALA 2 : 1; ACABADO:; REBARBAR Y; ROMPER ARISTAS; NO CAMBIE LA ESCALA; REVISIÓN; Landing Gear

En todas las

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

NOMBRE | FIRMA | FECHA | | TÍTULO: Snap para Lidar

DIBUJ.
VERIF.
APROB.
FABR.

MATERIAL: FIlamento de PLA o PET

DETALLE P ESCALA 2 : 1; ACABADO:; REBARBAR Y; ROMPER ARISTAS; NO CAMBIE LA ESCALA; REVISIÓN; Landing Gear

En todas las

SI NO SE INDICA LO CONTRARIO:
LAS COTAS SE EXPRESAN EN MM
ACABADO SUPERFICIAL:
TOLERANCIAS:
LINEAL: 0.25mm
ANGULAR: 1°

NOMBRE | FIRMA | FECHA | TÍTULO: SNAP

DIBUJ.
VERIF.
APROB.
FABR.

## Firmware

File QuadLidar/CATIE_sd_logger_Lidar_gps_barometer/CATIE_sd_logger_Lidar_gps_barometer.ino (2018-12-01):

#include <SPI.h>
#include <SD.h>
#include <Adafruit_BMP085.h>
#include <Wire.h>
#include <LIDARLite.h>

float myVal = 3.1415;

//GPS
#include "Ublox.h"
#define SERIAL_BAUD 115200
#define GPS_BAUD 9600
#define N_FLOATS 4

Ublox M8_Gps;
// Altitude - Latitude - Longitude - N Satellites
float gpsArray[N_FLOATS] = {0, 0, 0, 0};
//GPS


//Lidar
LIDARLite myLidarLite;

//BAROMETRO
Adafruit_BMP085 bmp;

// SD CARD Set the pins used
#define cardSelect 4

File logfile;

char filename[15];

// blink out an error code
void error(uint8_t errno) {
  while(1) {
    uint8_t i;
    for (i=0; i<errno; i++) {
      digitalWrite(13, HIGH);
      delay(100);
      digitalWrite(13, LOW);
      delay(100);
    }
    for (i=errno; i<10; i++) {
      delay(200);
    }
  }
}

void setup() {
  // connect at 115200 so we can read the GPS fast enough and echo without dropping chars
  // also spit it out
  Serial.begin(SERIAL_BAUD);
  Serial1.begin(GPS_BAUD);
  // Serial.println("\r\nAnalog logger test");
  pinMode(13, OUTPUT);

  //LIDAR
  myLidarLite.begin(0, true); // Set configuration to default and I2C to 400 kHz
  myLidarLite.configure(0); // Change this number to try out alternate configurations

  if (!bmp.begin()) {
  // Serial.println("Could not find a valid BMP085 sensor, check wiring!");
    error(2);
  }

  // see if the card is present and can be initialized:
  if (!SD.begin(cardSelect)) {
     Serial.println("Card init. failed!");
    error(2);
  }

  strcpy(filename, "CATIE_00.TXT");
  for (uint8_t i = 0; i < 100; i++) {
    filename[6] = '0' + i/10;
    filename[7] = '0' + i%10;
    // create if does not exist, do not open existing, write, sync after write
    if (! SD.exists(filename)) {
      break;
    }
  }

  logfile = SD.open(filename, FILE_WRITE);
  if( ! logfile ) {
    // Serial.print("Couldnt create "); 
    // Serial.println(filename);
    error(3);
  }
  // Serial.print("Writing to "); 
  // Serial.println(filename);

  pinMode(13, OUTPUT);
  pinMode(8, OUTPUT);
  // Serial.println("Ready!");

}

uint8_t i=0;
void loop() {
  String dataString = "";
  
  while(Serial1.available()){
        char c = Serial1.read();
        //Serial.println(c);
         if (M8_Gps.encode(c)) {
          gpsArray[0] = M8_Gps.altitude;
          gpsArray[1] = M8_Gps.latitude;
          gpsArray[2] = M8_Gps.longitude;
           
          gpsArray[3] = M8_Gps.sats_in_use;

        }
  }

  //LEER BAROMETRO
  //dataString = bmp.readTemperature();
  //dataString += ",";
//  dataString += bmp.readPressure();
//  dataString += ",";
  dataString += String(gpsArray[1],10);
  dataString += ",";
  dataString += String(gpsArray[2],10);
  dataString += ",";
  dataString += String(gpsArray[0],10);
  dataString += ",";
  dataString +=bmp.readAltitude();
  dataString += ",";
//  dataString += bmp.readSealevelPressure();
//  dataString += ",";
//  dataString += bmp.readAltitude(101500);
//  dataString += ",";
  dataString += myLidarLite.distance(false);
  dataString += ",";
  dataString += gpsArray[3];
  
  digitalWrite(8, HIGH);

  //Guardamos datos
  logfile = SD.open(filename, FILE_WRITE);
  
  logfile.println(dataString);
  logfile.close();
  Serial.println(dataString);

}

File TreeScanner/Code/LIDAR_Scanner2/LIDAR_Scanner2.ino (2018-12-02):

#include <Wire.h>
#include <Adafruit_Sensor.h>
#include <Adafruit_LSM303_U.h>
#include <Adafruit_L3GD20_U.h>
#include <Adafruit_9DOF.h>
#include <LIDARLite.h>
#include <Servo.h>

#define ACCEL 150
#define SERVOPIN 13


/* Assign a unique ID to the sensors */
Adafruit_9DOF                dof   = Adafruit_9DOF();
Adafruit_LSM303_Accel_Unified accel = Adafruit_LSM303_Accel_Unified(30301);
Adafruit_LSM303_Mag_Unified   mag   = Adafruit_LSM303_Mag_Unified(30302);

/* Update this with the correct SLP for accurate altitude measurements */
float seaLevelPressure = SENSORS_PRESSURE_SEALEVELHPA;

Servo servo;
LIDARLite myLidarLite;

/**************************************************************************/
/*!
    @brief  Initialises all the sensors used by this example
*/
/**************************************************************************/
void initSensors()
{
  if (!accel.begin())
  {
    /* There was a problem detecting the LSM303 ... check your connections */
    Serial.println(F("Ooops, no LSM303 detected ... Check your wiring!"));
    while (1);
  }
  if (!mag.begin())
  {
    /* There was a problem detecting the LSM303 ... check your connections */
    Serial.println("Ooops, no LSM303 detected ... Check your wiring!");
    while (1);
  }
}

/**************************************************************************/
/*!

*/
/**************************************************************************/
void setup(void)
{
  Serial.begin(9600);
  Serial.println(F("Adafruit 9 DOF Pitch/Roll/Heading Example")); Serial.println("");

  /* Initialise the sensors */
  initSensors();
  //setMotors();
  myLidarLite.begin(0, true);
  myLidarLite.configure(5);
  servo.attach(SERVOPIN);
  pinMode(5, OUTPUT);
  pinMode(10, OUTPUT);
  digitalWrite(5, HIGH);
  digitalWrite(10, LOW);

}

/**************************************************************************/
/*!
    @brief  Constantly check the roll/pitch/heading/altitude/temperature
*/
/**************************************************************************/
void loop(void)
{
  servo.write(0);
  sensors_event_t mag_event;
  sensors_vec_t   orientation;


  /* Calculate the heading using the magnetometer */
  mag.getEvent(&mag_event);

  if (dof.magGetOrientation(SENSOR_AXIS_Z, &mag_event, &orientation))
  {
    /* 'orientation' should have valid .heading data now */
    Serial.print(orientation.heading);
    Serial.print(F(", "));
  }

  Serial.println(myLidarLite.distance());
  delay(100);
}

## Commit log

2018-11-29 Archivos para corte laser e impresion 3D
    [27_ja_21_kulmamittari.stl, 8.5_asteen_kulmamittari.stl, Cameratray.stl, ft_mini_horn.stl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]
2018-12-01 Fotos y codigo de lidar
    [Base snap batería.STL, Chasis atrás derecho.STL, Chasis atrás izquierdo.STL, Soporte Baterías.STL]
